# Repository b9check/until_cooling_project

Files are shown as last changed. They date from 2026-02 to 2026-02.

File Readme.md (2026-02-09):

# Organ Perfusion Thermal Control

Simulation of a mobile perfusion system for loading cryoprotective agents (CPA) into porcine kidneys during transport. Developed for Until Labs.

## Problem

Maintain 4°C ± 2°C at the kidney inlet while flow varies 10× (3-30 mL/min) due to pressure control. A flow-dependent transport delay (1-11s) between heater and sensor makes pure PI control fail.

## Solution

Feedforward + PI: feedforward computes heater power from flow rate (P = ṁ·Cp·ΔT), PI trims residual error.

## Results

- Temp max error: 0.23°C (spec ±2°C) ✓
- Pressure max error: 0.87 mmHg (spec ±3 mmHg) ✓

## Files

**Simulation (Task 1):**
- main.m - Full 30-min simulation
- run_simulation.m - Physics + control loop
- heater_dynamics.m - NTU-effectiveness thermal model
- Pure_PI.m - PI without transport delay (baseline)
- Pure_PI_Lag.m - PI with delay, no feedforward (fails)
- plot_dynamics.m - Heater response visualization

**CAD:**
- CAD/Cooling Machine/ - Task 1: Mobile perfusion system
- CAD/Cradle/ - Task 2: Organ cradle

## Author

Brian Check - Stanford MS Aero/Astro

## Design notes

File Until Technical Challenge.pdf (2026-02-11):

# Until Take Home Project

# Brian Check Files available on GitHub (https://github.com/b9check/until_cooling_project/tree/main)

# Presentation Overview

## Task 1: Mobile CPA Loading System 1. Problem Overview 2. System Architecture 3. Controller Design and Simulation 4. Hardware Overview

## Task 2: Cradle Design 1. Task Overview 2. Design Overview 3. BOM

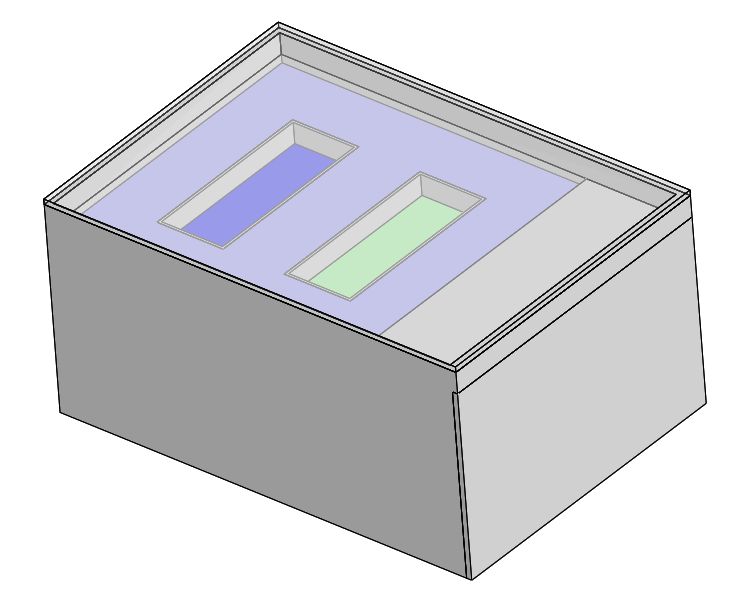
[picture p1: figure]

# Task 1 Mobile CPA Loading System

# Task Overview

## Challenge

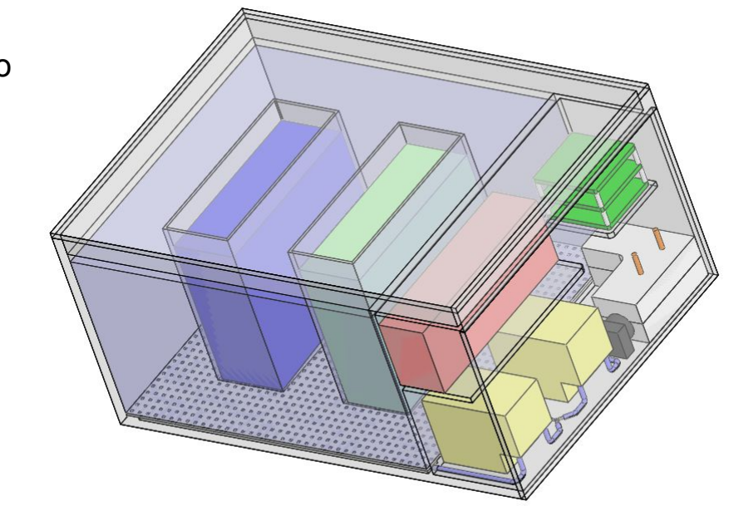
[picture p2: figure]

## - Design mobile system to load cryoprotectants into porcine kidneys during transport

## Requirements - Temperature: 4°C ± 2°C - Pressure: 30 mmHg ± 3 mmHg - Variable flow: 3-30 mL/min - Two-fluid mixing a. Carrier + CPA, ramping up CPA over time - Single-pass perfusion - ~2 hour runtime, battery powered

# Domain Research and Benchmarking

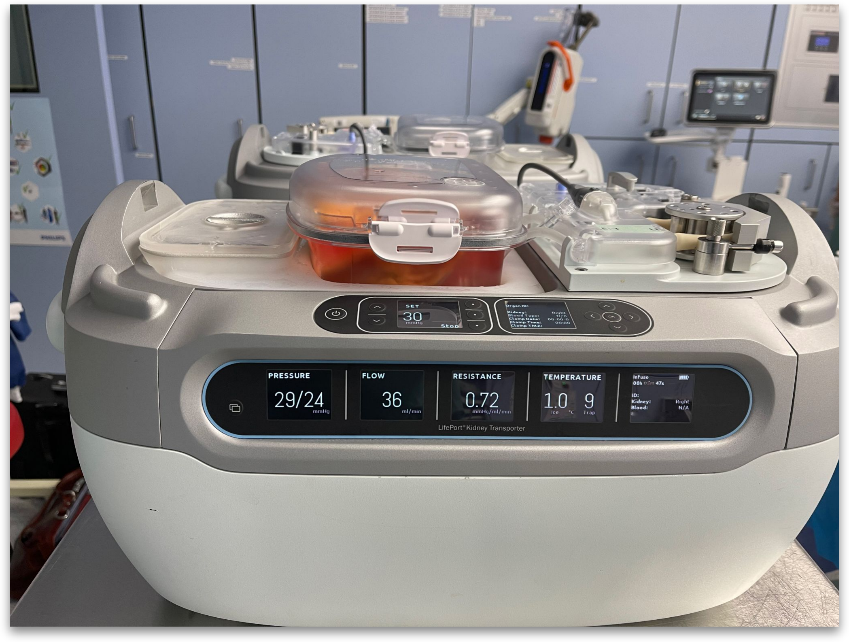
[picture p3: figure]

LifePort Kidney Transporter (https://www.organ-recovery.com/lifeport-kidney-transporter/) - gold standard for clinical kidney transport

## - Pulsatile flow, pressure control, recirculating - Passive cooling with ice bath

## LifePort keeps organs cold, but doesn't meet Until's requirements:

## - Cooling: passively controlled, ~2-10°C (not 4±2°C precision) - Recirculating flow (not single-pass) - Limited to hypothermic preservation (no CPA loading capability)

Key Takeaway: Until's challenge requires active temperature control with single-pass perfusion during CPA concentration ramping
- fundamentally different operating regime than existing clinical transporters

# System Architecture

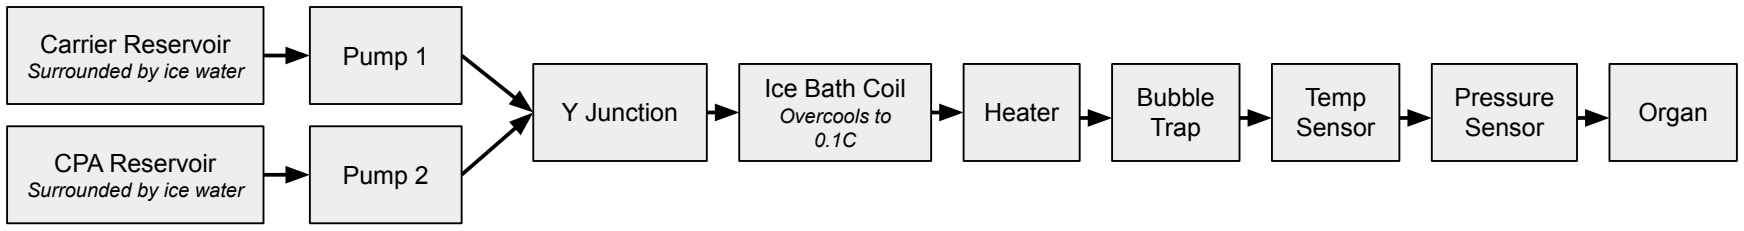
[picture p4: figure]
CPA Reservoir; Surrounded by ice water; Carrier Reservoir; Pump 2; Pump 1; Y Junction; Ice Bath Coil; Overcools to 0.1C; Heater; Bubble; Trap; Temp Sensor; Pressure; Sensor; Organ

### How I got here

The Fundamental Challenge
- To hold ±2°C, you need closed-loop control. Closed-loop control requires an actuator you can modulate
- How do you actively control temperature in a fluid line?
- Peltier/TEC: Bulky, power-hungry, complex heat rejection
- Recirculating chiller: Not mobile - requires benchtop equipment
- Variable ice contact: No practical way to modulate heat transfer dynamically

The realization
- Cooling is hard to modulate. But heating is trivial - a resistive heater with PWM gives you precise, instantaneous control.

The architecture flip
- Instead of trying to cool precisely to 4°C, overcool past the setpoint, then heat back up.

# System Architecture - Layout [Overcooling]

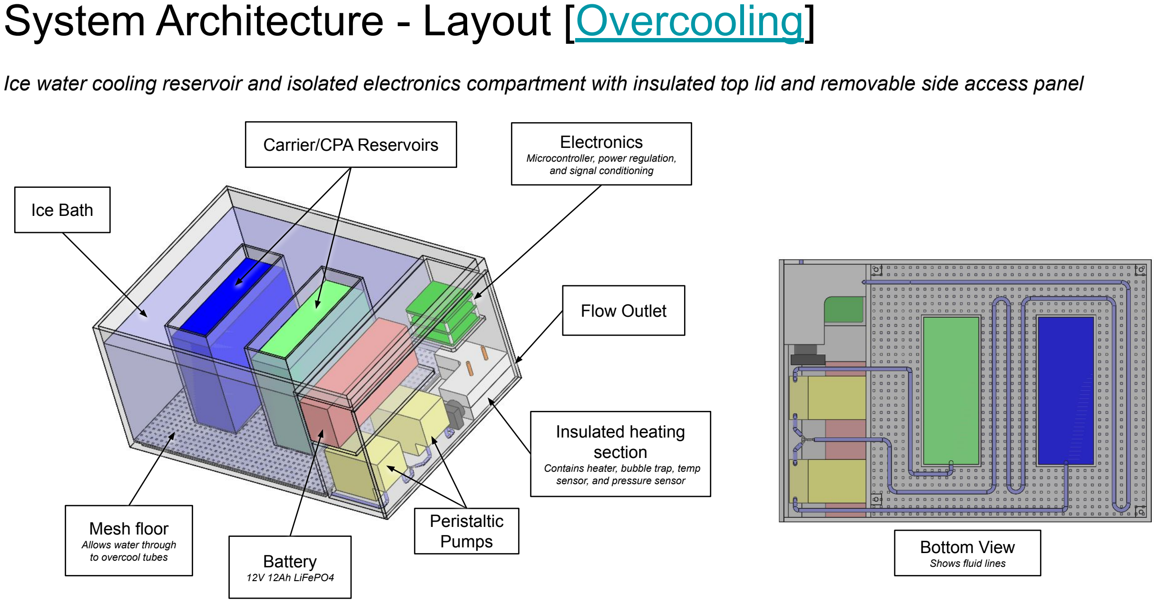
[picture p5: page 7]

Ice Bath

Carrier/CPA Reservoirs

Mesh floor

Allows water through
to overcool tubes

Bottom View

Shows fluid lines

Peristaltic
Pumps

Ice water cooling reservoir and isolated electronics compartment with insulated top lid and removable side access panel

Insulated heating
section

Contains heater, bubble trap, temp sensor, and pressure sensor

Electronics

Microcontroller, power regulation, and signal conditioning

Battery

12V 12Ah LiFePO4

Flow Outlet

# Control: Setup & Challenge

Two independent control loops:

- Pressure → Pump speed (sets flow rate)
- Temperature → Heater power (compensates for varying flow)

Challenge: Flow varies 10x during protocol - heater must maintain 4°C regardless despite temp being coupled with flow speed

# Simulation Setup [Pseudocode]

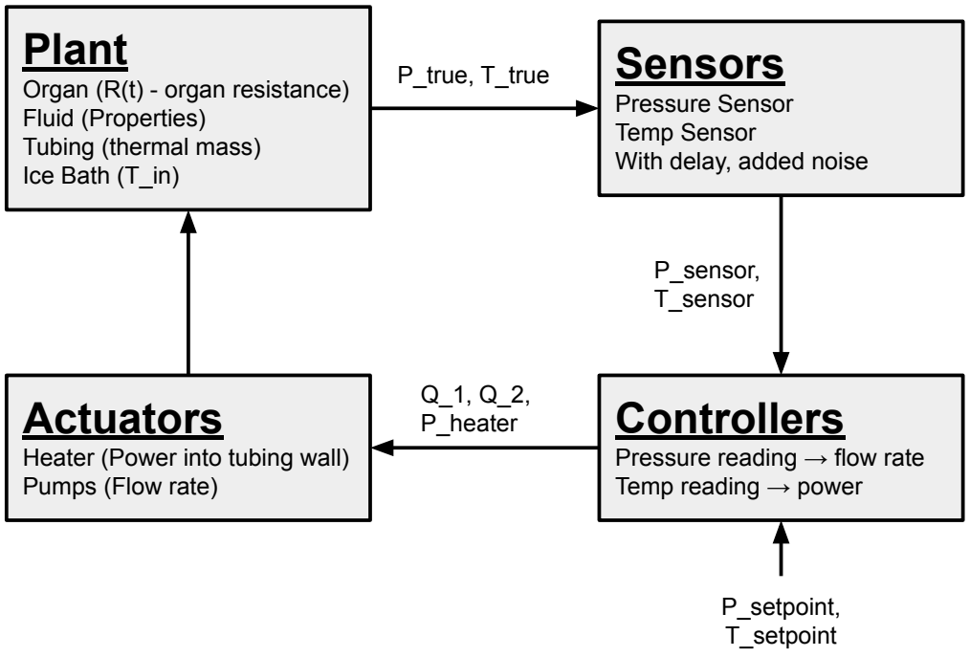
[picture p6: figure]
Plant; Organ (R(t) - organ resistance) Fluid (Properties) Tubing (thermal mass) Ice Bath (T_in); Sensors; Pressure Sensor Temp Sensor With delay, added noise; Controllers; Pressure reading → flow rate Temp reading → power; Actuators; Heater (Power into tubing wall) Pumps (Flow rate); P_true, T_true; P_sensor, T_sensor; Q_1, Q_2, P_heater; P_setpoint, T_setpoint

Setpoints (targets):
- P_setpoint, T_setpoint
Disturbances:
- R(t) - organ resistance changing over time
- T_in - cold fluid from ice bath
Measured (controller inputs):
- P_sensor
- T_sensor
Commanded (controller outputs):
- Q_total → split to pumps
- P_heater → to heater
States (internal dynamics):
- T_wall — tubing wall temperature
- P_integral, T_integral — controller memory Outputs (what you care about):
- P_true — actual organ perfusion pressure
- T_out — actual fluid temperature to organ

# Heat Transfer: Transient Dynamics Model [More Detail]

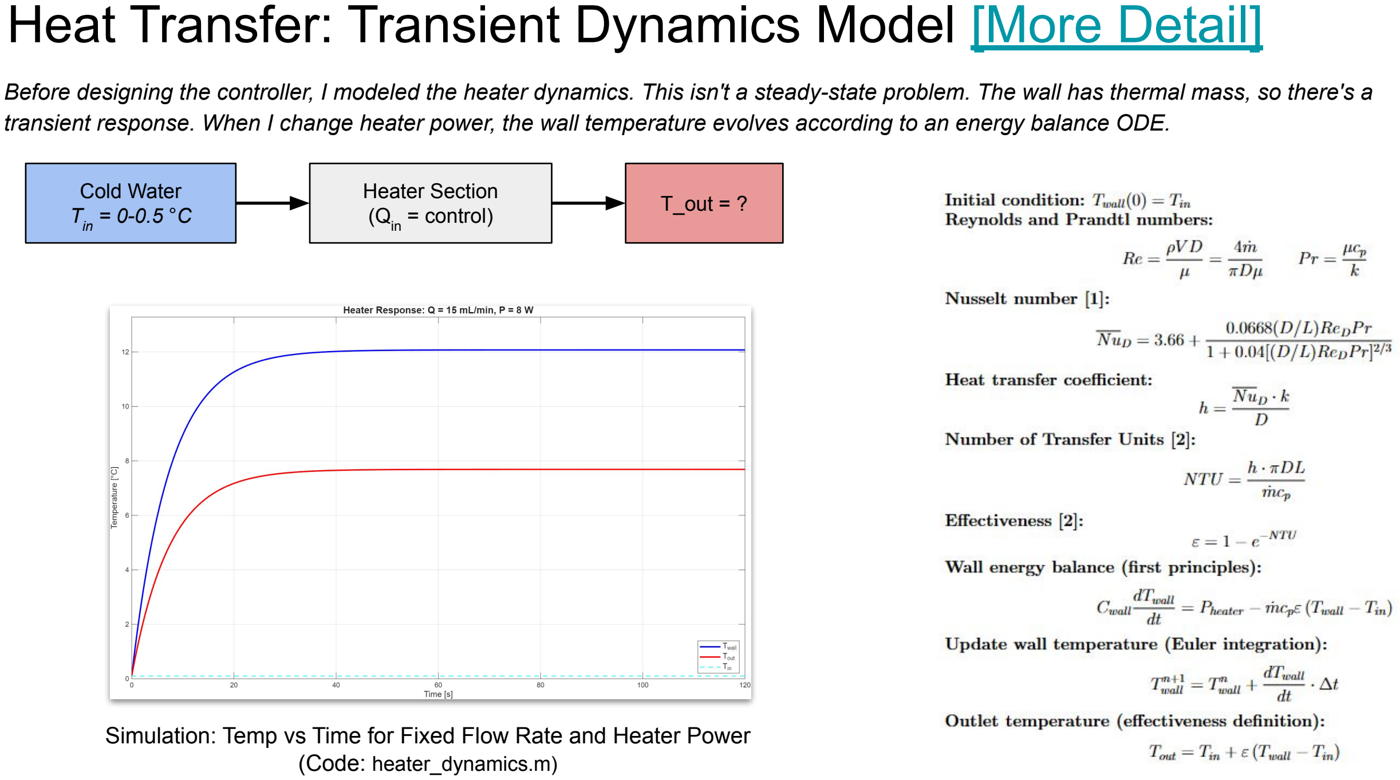
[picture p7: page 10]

Before designing the controller, I modeled the heater dynamics. This isn't a steady-state problem. The wall has thermal mass, so there's a transient response. When I change heater power, the wall temperature evolves according to an energy balance ODE.

Cold Water
Tin = 0-0.5 °C

Heater Section
(Qin = control) | T_out = ?

Simulation: Temp vs Time for Fixed Flow Rate and Heater Power (Code: heater_dynamics.m)

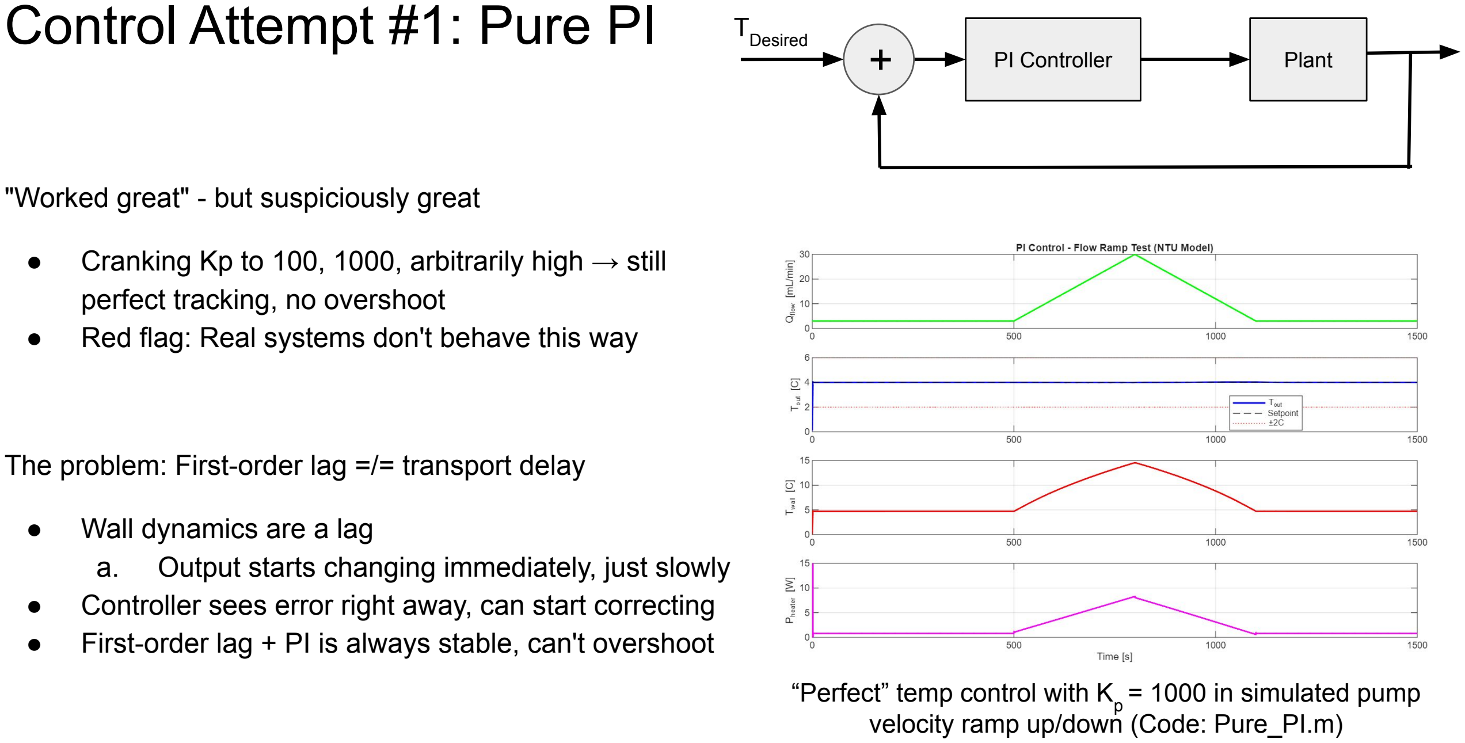
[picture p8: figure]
Control Attempt #1: Pure PI; PI Controller; TDesired; Plant; "Worked great" - but suspiciously great; perfect tracking, no overshoot; ● Wall dynamics are a lag; velocity ramp up/down (Code: Pure_PI.m)

### - Cranking Kp to 100, 1000, arbitrarily high → still

### - Red flag: Real systems don't behave this way

### The problem: First-order lag =/= transport delay

### a. Output starts changing immediately, just slowly - Controller sees error right away, can start correcting - First-order lag + PI is always stable, can't overshoot

### “Perfect” temp control with Kp = 1000 in simulated pump

# Control Attempt #2: Pure PI with Added Transport Delay

A Realization

- Sensor located 8 cm downstream of heater
- Transport delay = tube volume / flow rate
- At 30 mL/min: 1.1 s delay
- At 3 mL/min: 11.3 s delay
- PI now controlling based on stale information
- Variable delay makes tuning impossible - gains that work at high flow oscillate at low flow

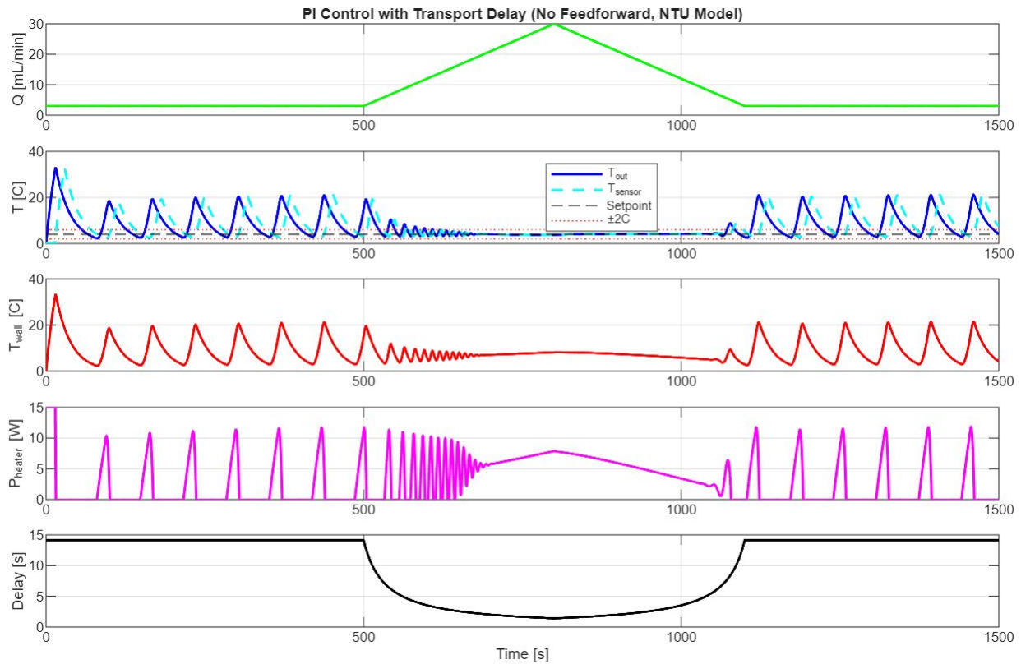
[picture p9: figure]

### Adding delay to sensor input blew up controller (Code: Pure_PI_Lag.m)

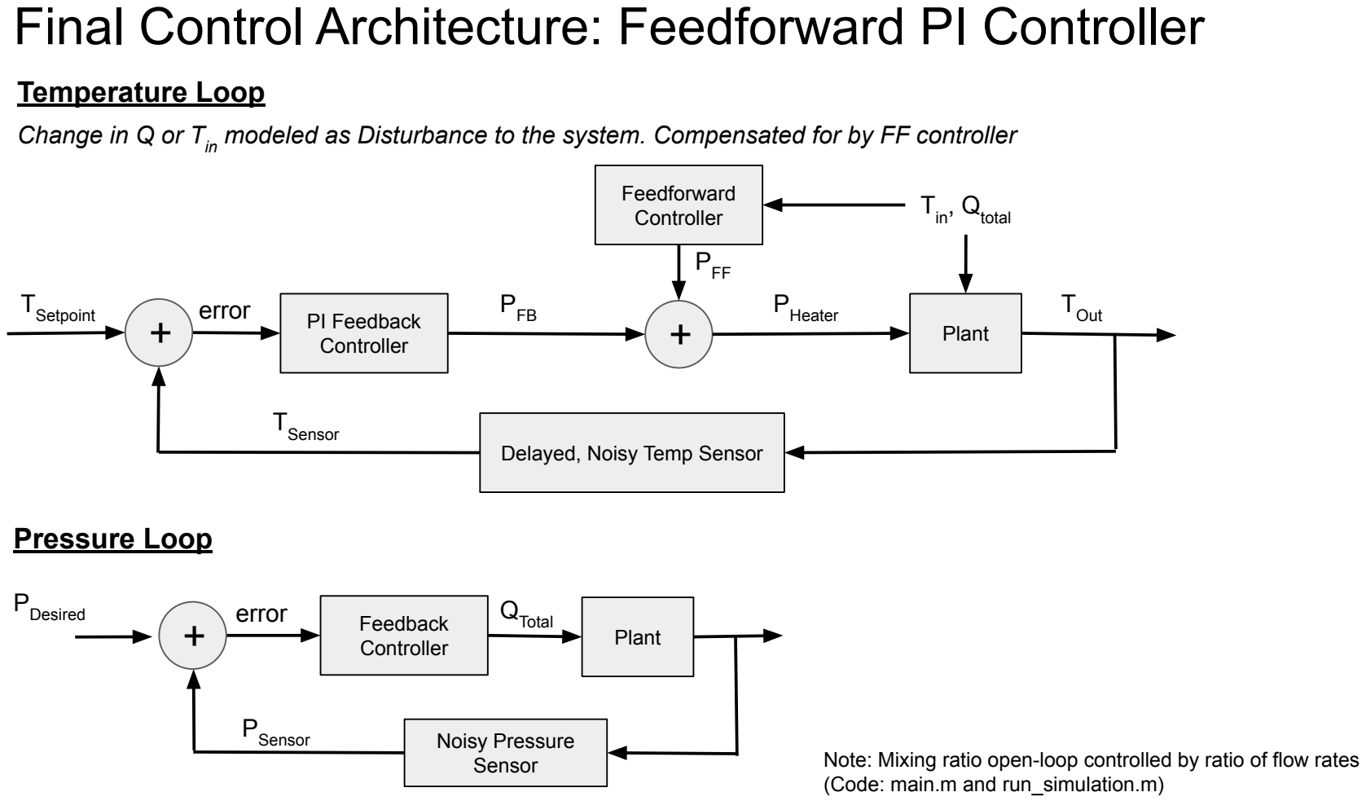
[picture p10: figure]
PI Feedback Controller; TSetpoint; Plant; Tin, Qtotal; Feedforward Controller; Delayed, Noisy Temp Sensor; TOut; Temperature Loop; Pressure Loop; Feedback Controller; PDesired; (Code: main.m and run_simulation.m); Noisy Pressure Sensor; PFB; PFF; PHeater; TSensor; QTotal; PSensor; error

# Final Control Architecture: Feedforward PI Controller

Change in Q or Tin modeled as Disturbance to the system. Compensated for by FF controller

Note: Mixing ratio open-loop controlled by ratio of flow rates

# Simulation Setup

## 30 min protocol: equilibrate → ramp CPA 0→70% Disturbances modeled: - Vascular resistance: 9 → 2 mmHg/(mL/min) (organ relaxes) a. P = Q x R - Pressure adjusts accordingly - Ice bath drift: +1°C over 30 min

- | Sensor noise/bias: Temp (https://pendotech.com/pendotech-products/sensors-and-monitors/temperature-sensors-monitors/) (σ=0.1°C, bias=0.1°C), | pressure (https://www.graylinemedical.com/products/edwards-lifesciences-truwave-disposable-pressure-transducer-kits-tru-wave-single-line-px-disposable-pressure-transduc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) (σ=0.3 mmHg, bias=0.5 mmHg)

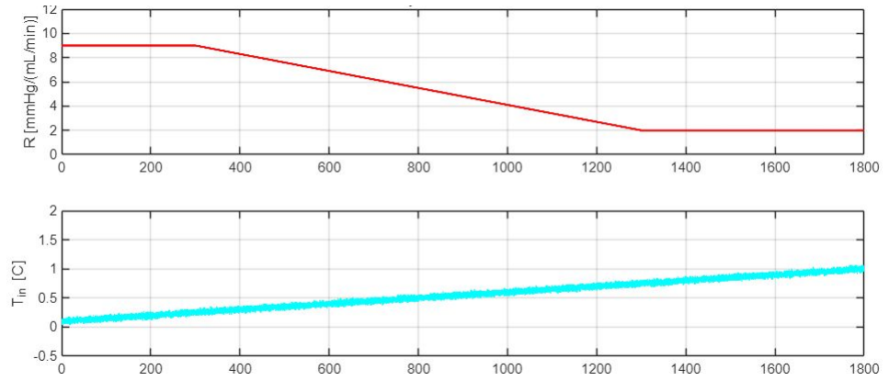
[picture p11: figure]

### Environmental changes to ice bath and organ resistance over simulation

# Simulation Results - Plots

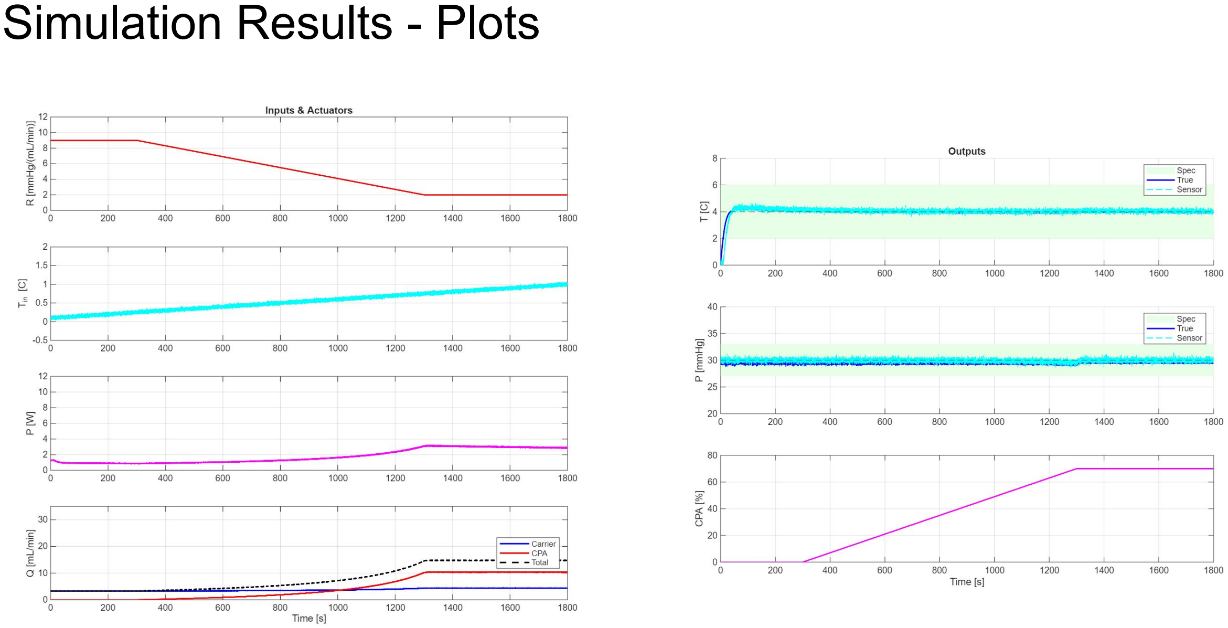
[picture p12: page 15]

# Simulation - Results and Limitations

Metric | Result | Spec
Temp max error | 0.2°C | ±2°C
Temp mean error | 0.06°C | —
Pressure max error | 1.1 mmHg | ±3 mmHg
Pressure mean error | 0.56 mmHg | —
In spec | 100% | —
Heater power | 3.2 W max, 1.8 W mean

### Limitations

- FF uses same thermal model as plant → results are optimistic.

### a. Real system will have model mismatch, would require tuning b. Cp varies with CPA%, heater efficiency - PI gains need tuning on hardware - Not modeled: bubbles, pump pulsation, startup transients - TLDR; have to tune IRL

# Hardware Overview

# Insulated lid, removable electronics panel

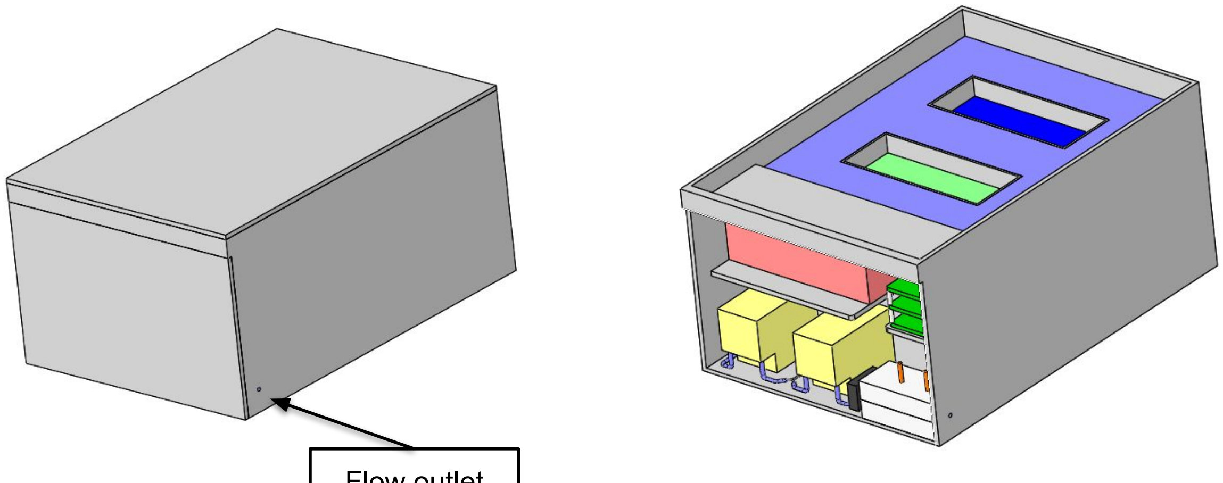
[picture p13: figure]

## Flow outlet

# Hardware Overview - Plumbing (Top view, no ice water)

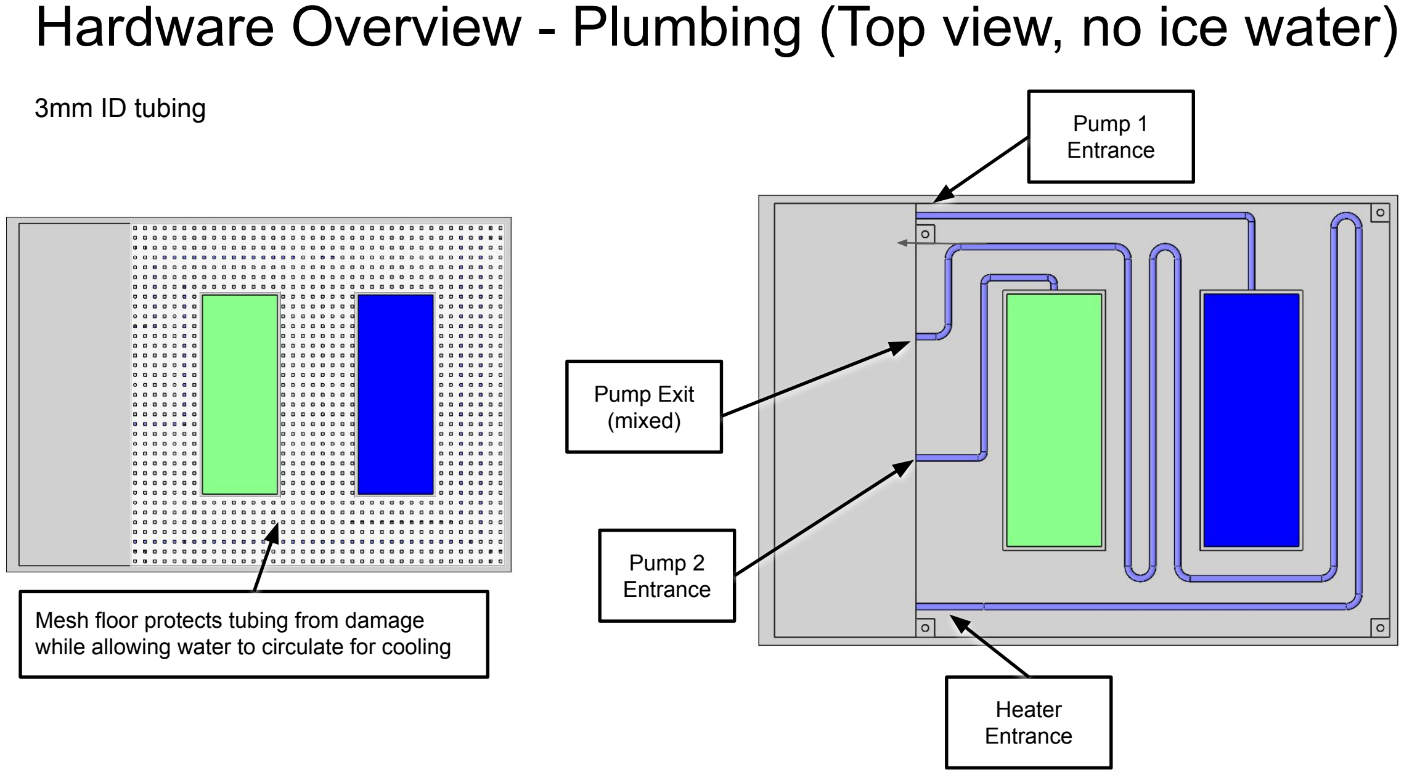
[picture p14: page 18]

Heater
Entrance

Mesh floor protects tubing from damage while allowing water to circulate for cooling

Pump Exit
(mixed)

Pump 1
Entrance

Pump 2
Entrance

### 3mm ID tubing

# Hardware Overview - Electronics

### Components

- Temp Sensor (https://pendotech.com/pendotech-products/sensors-and-monitors/temperature-sensors-monitors/)
- Pressure Sensor (https://www.graylinemedical.com/products/edwards-lifesciences-truwave-disposable-pressure-transducer-kits-tru-wave-single-line-px-disposable-pressure-transduc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)
- Heater (https://keenovo.store/products/keenovo-silicone-heater-strip-pipe-tube-line-heating-band-belt-1) (wrapped around tube)

### - Battery (https://www.dxengineering.com/parts/bip-blf-1212a?seid=dxese1)

- Bubble Trap (https://elveflow.com/microfluidic-products/microfluidics-accessories/bubble-remover/)

### - Y fitting (https://www.mcmaster.com/5372K903/) - T100-WX10 OEM Peristaltic Pump (https://www.longerpump.com/list_62/693.html) - Arduino/ESP32 Microcontroller

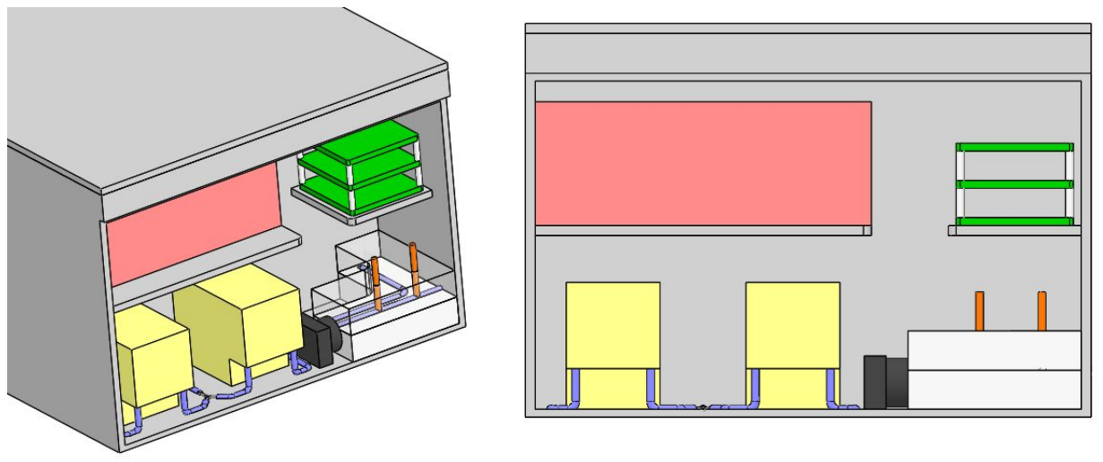
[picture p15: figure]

### Power: 20W typical, 35W max - Heater: 3W - Pumps: 2x 12W max - Controller/Sensors: ~5W

### Size: 14.3" × 20.2" × 9.9"

### Next Steps - Power distribution (12V → 5V/3.3V) - Signal conditioning - Battery charging - Mechanical DFM/DFA

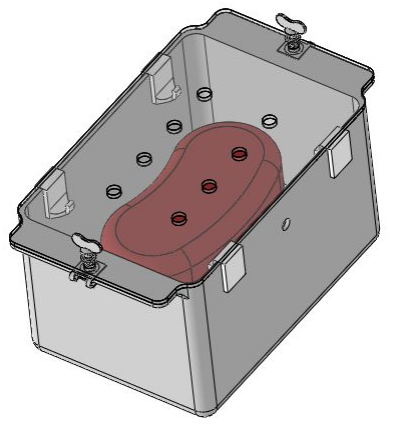
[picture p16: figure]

# Task 2 Cradle

# Task 2

## Requirements

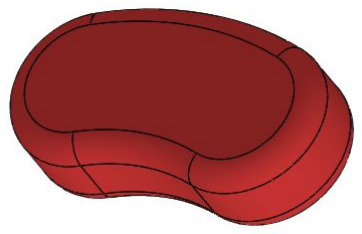
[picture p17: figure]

## - Compliantly hold adult pig kidney in sealed bag - Fit within 8" diameter × 12" length cylinder - 9 sealable ports for fluid/probe access - Arterial cannula at 90° to kidney

## Kidney sizing (3σ range) [Source]

## - Length: 92 - 148 mm - Width: 37 - 77 mm - Thickness: 14 - 41 mm

## Design envelope

## - Fits largest kidney + margin for bag + effluent pool

# Design Overview

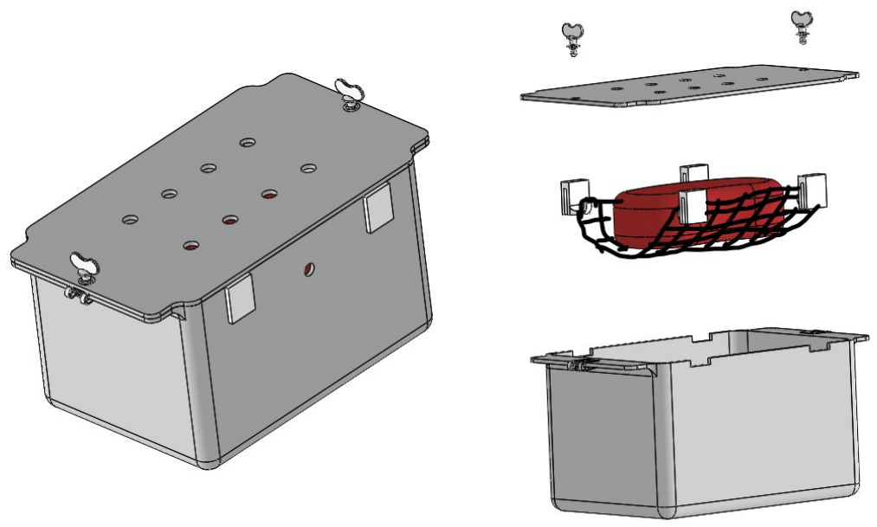
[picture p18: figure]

### Features - Rectangular box with flanged rim - Removable lid with 8 luer ports a. 9th port on side wall - Mesh sling suspended from hooks on rim - Press fit hooks slide onto box - Cannula holder on side wall (90° to kidney) - Quarter-turn latches secure lid

# It Fits! Dimensions: 5.75” x 10” x 5.5”

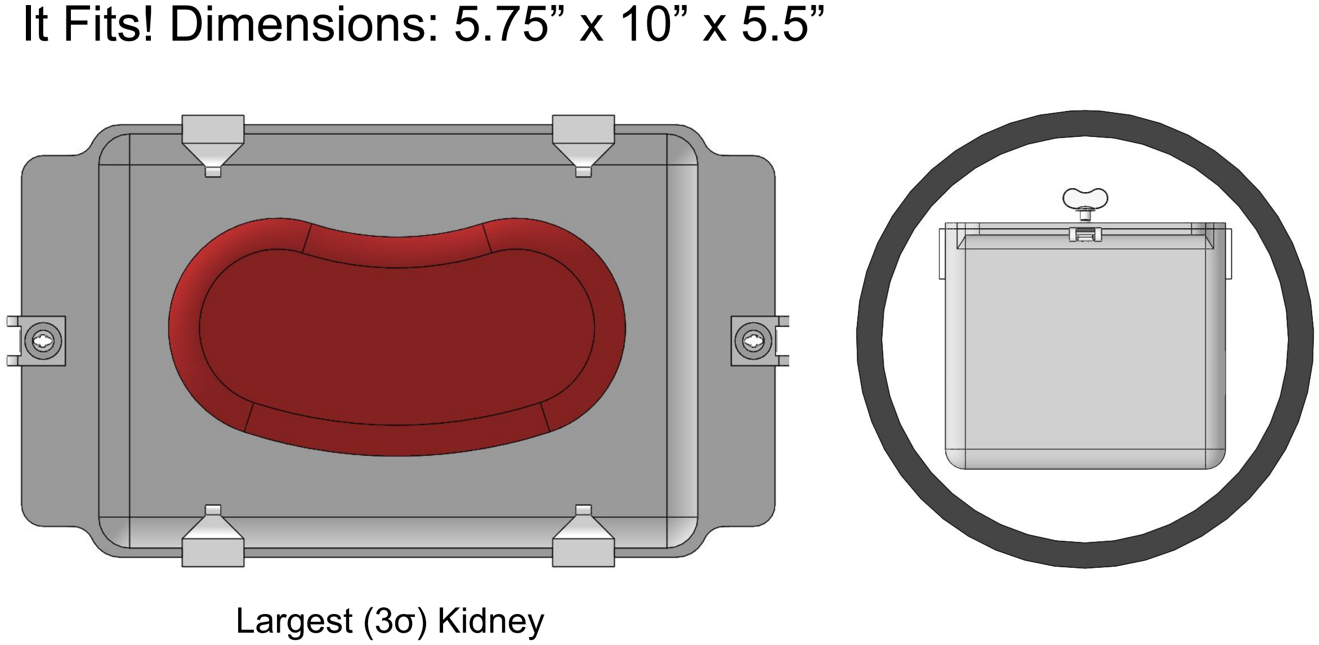
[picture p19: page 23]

# Largest (3σ) Kidney

# BOM, Materials, and Manufacturing

Part | Qty | Prototype Mfg Method | Production Mfg Method
Box | 1 | SLS Tough, print upright | Injection molded PP
Lid | 1 | SLA Tough, print flat | Injection molded PP
Mesh hooks | 4 | SLA Tough, print on side | Injection molded PP
Mesh sling | 1 | Off-the-shelf | Off-the-shelf
Port fittings | 9 | Off-the-shelf luer | Same
Quarter turn fasteners | 2 | McMaster 91382A350 | Off-the-shelf

# Appendix

# Controller Simulation Loop Pseudocode [Go Back]

Inputs
- Set R from protocol schedule
- Set cpa_ratio from protocol schedule → update fluid properties (ρ, Cp, k, μ)
- Update T_in from ice bath model

Pressure control → (True pressure → Pressure sensor reading → Flow speeds)
- P_true = Q_total(i-1) x R
- P_sensor = P_true + bias + noise
- P_error = P_setpoint - P_sensor
- Q_total = Q_nominal + Kp x P_error + Ki x P_integral
- Clamp Q_total to [Q_min, Q_max] with anti-windup
- Split: Q_cpa = Q_total x cpa_ratio, Q_carrier = Q_total x (1 - cpa_ratio)

Temperature control → (True temp → Temp sensor reading → Heater power)
- T_out = heater_dynamics(T_in, T_wall, Q_total, P_heater, fluid, ...)
- delay_samples = V_sensor / Q / dt (quasi-steady approximation)
- T_sensor = T_out(delayed) + bias + noise
- T_error = T_setpoint - T_sensor
- P_ff = ṁ x Cp x (T_setpoint - T_in) (steady-state feedforward)
- P_fb = Kp x T_error + Ki x T_integral
- P_heater = P_ff + P_fb
- Clamp P_heater to [0, P_max] with anti-windup

Plant update:
- T_wall += dT_wall/dt × dt (from heater_dynamics)

# Overcooling [Go Back]

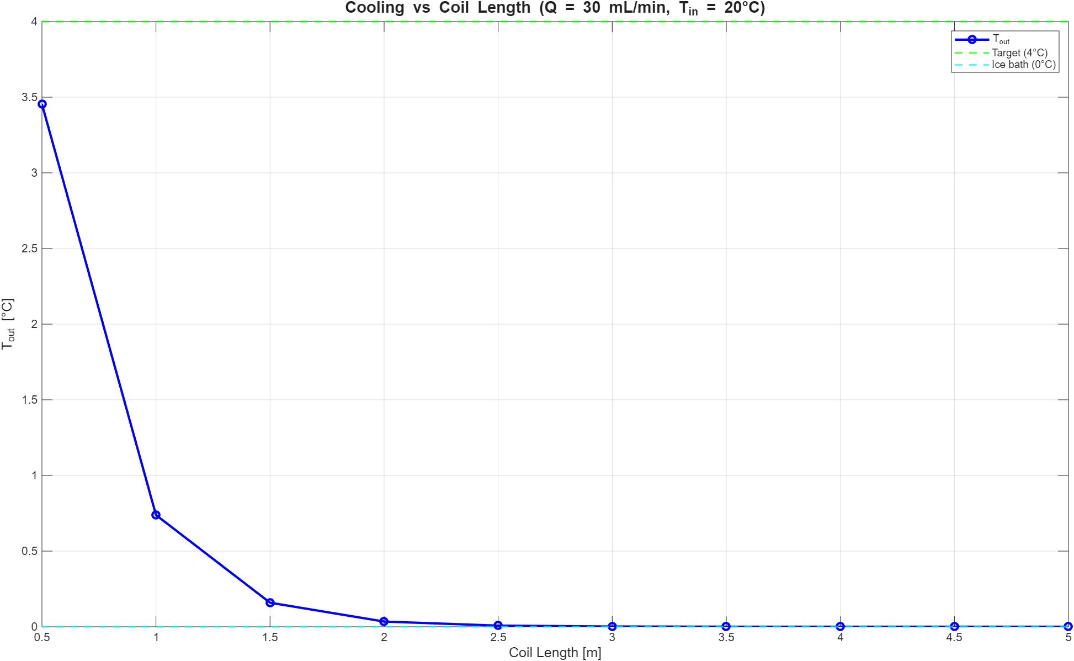
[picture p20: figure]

# 3D Printing Method Selection

| SLS (PA12) | SLA (Resin) | FDM (PLA/ABS)
Strength | High | Low | Med
Surface Finish | Med | High | Low
Watertight | High | High | Low
Large Parts | High | Low | High
Thin Walls | High | Low | Low
Biocompatibility | Med | Med | Low
Tolerance | Med | High | Low
Flexibility | Med | Low | Med

# Heat Transfer Calculations [Go Back]

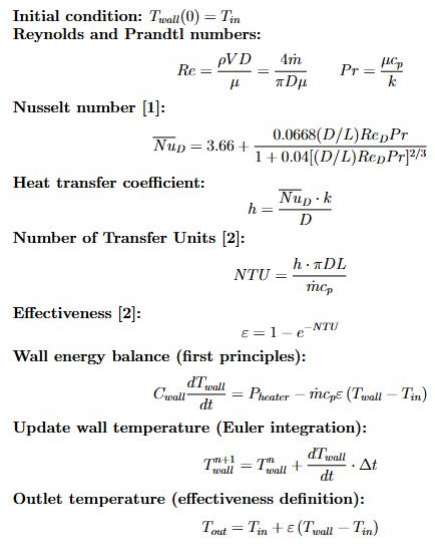
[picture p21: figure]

Inputs:
- Geometry: D (tube diameter), L (heated length)
- Fluid properties: ρ, μ, cp, k (functions of CPA concentration)
- Operating conditions: mdot (mass flow rate), Tin (inlet temperature), Pheater (heater power)
- Thermal mass: Cwall (wall thermal capacitance)

Assumptions:
- Laminar flow
- Fully developed velocity profile, developing thermal profile
- Lumped wall thermal mass (uniform Twall over heater length)
- Negligible axial conduction in fluid
- Cr = 0 (wall thermal capacity ≫ fluid capacity in heater section)

This is a first-principles thermal model. The heater wall has thermal mass - it stores energy. When I apply power, the wall heats up, and heat transfers to the fluid based on the NTU-effectiveness relationship. The key thing is that the dynamics depend on flow rate: at high flow, the fluid pulls heat away faster, so the wall responds differently than at low flow. This is a nonlinear, flow-dependent system.

# Pig Kidney: Worst Case Dimensions (+-3σ) [Go Back]

Dimension | Mean | SD | Smallest (−3σ) | Largest (+3σ)
Length | 120 | 9.2 | 92.4 | 147.6
Width (cranial pole) | 56.9 | 6.7 | 36.8 | 77.0
Width (hilum) | 52.6 | 6.1 | 34.3 | 70.9
Width (caudal pole) | 52.4 | 6.7 | 32.3 | 72.5
Thickness | 27.9 | 4.5 | 14.4 | 41.4

All dimensions in mm
Max: Roughly a 148x77x41 bean

# Sources

1. Incropera, F.P., DeWitt, D.P., Bergman, T.L., Lavine, A.S. Fundamentals of Heat and Mass Transfer, 7th ed., Wiley, 2011, Eq. 8.57, p. 517
a. For heat transfer basics
2. Kays, W.M. \& London, A.L. Compact Heat Exchangers, 3rd ed., McGraw-Hill, 1984, Ch. 2, pp. 19-24
a. For NTU effectiveness calculations to model changing wall temperature
3. Gómez FA, Ballesteros LE, Estupiñán HY. Anatomical study of the renal excretory system in pigs. A review of its characteristics as compared to its human counterpart. Folia Morphologica. 2017;76(2):262–268. doi:10.5603/FM.a2016.0065
a. For pig kidney size

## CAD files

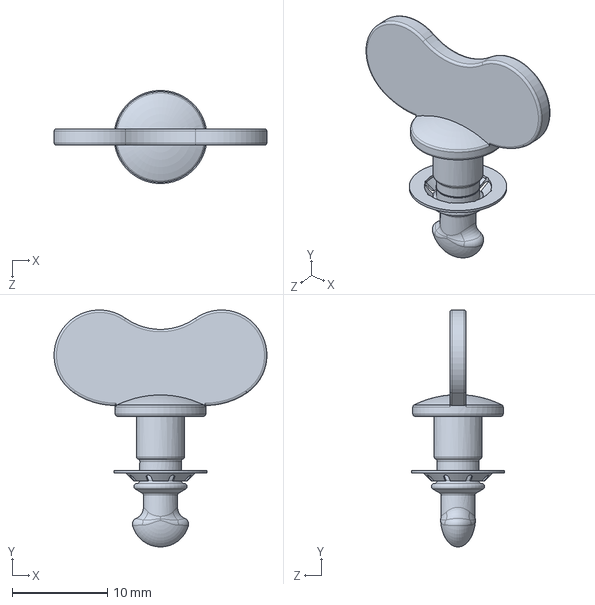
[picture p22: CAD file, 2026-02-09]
CAD/Cradle/Dzus-Fastener.SLDPRT
22.3 x 24.9 x 9.77 mm

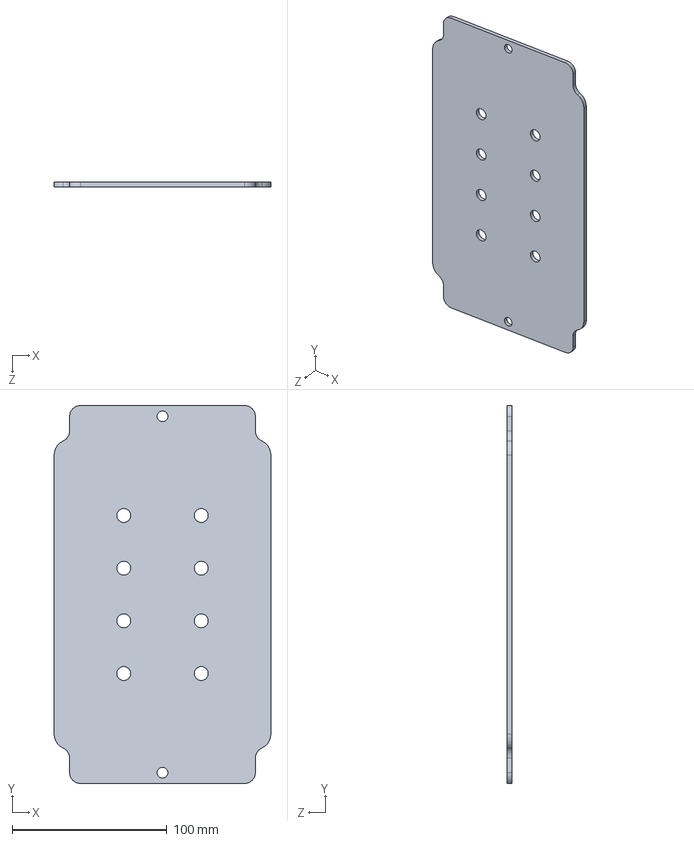
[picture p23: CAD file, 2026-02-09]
CAD/Cradle/cradle_lid.SLDPRT
140.0 x 244.0 x 3.00 mm

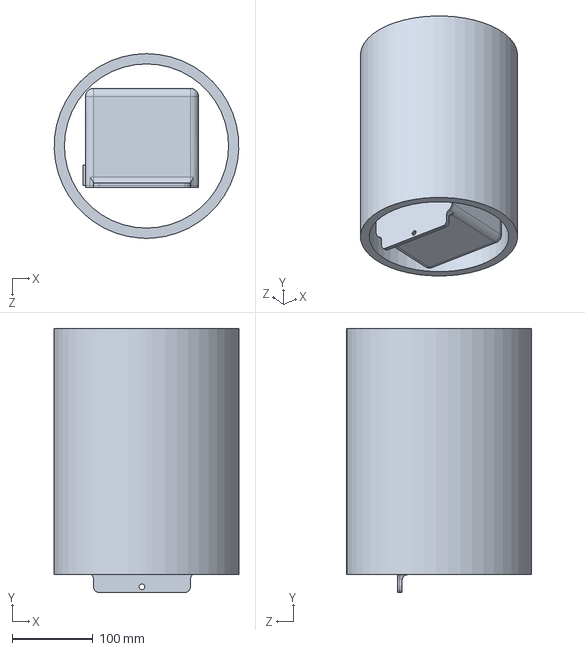
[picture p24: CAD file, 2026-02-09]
CAD/Cradle/cradle.SLDPRT
228.5 x 326.8 x 228.6 mm

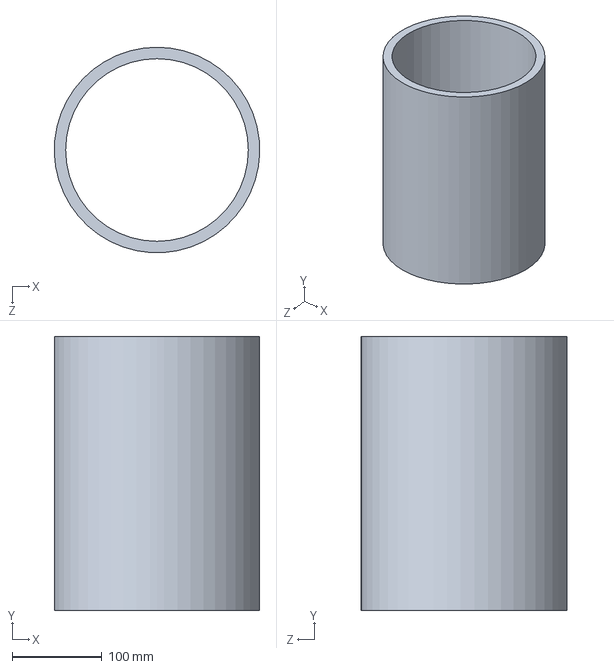
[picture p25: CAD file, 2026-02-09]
CAD/Cradle/cradle_cylilnder.SLDPRT
228.5 x 304.8 x 228.6 mm

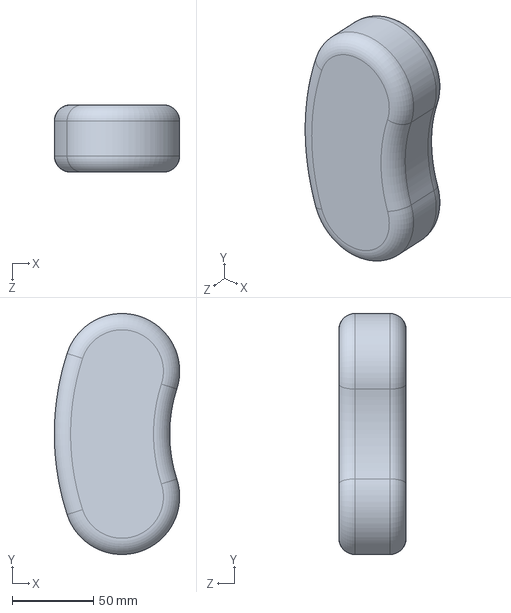
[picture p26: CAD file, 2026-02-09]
CAD/Cradle/kidney.SLDPRT
77.0 x 148.0 x 41.4 mm

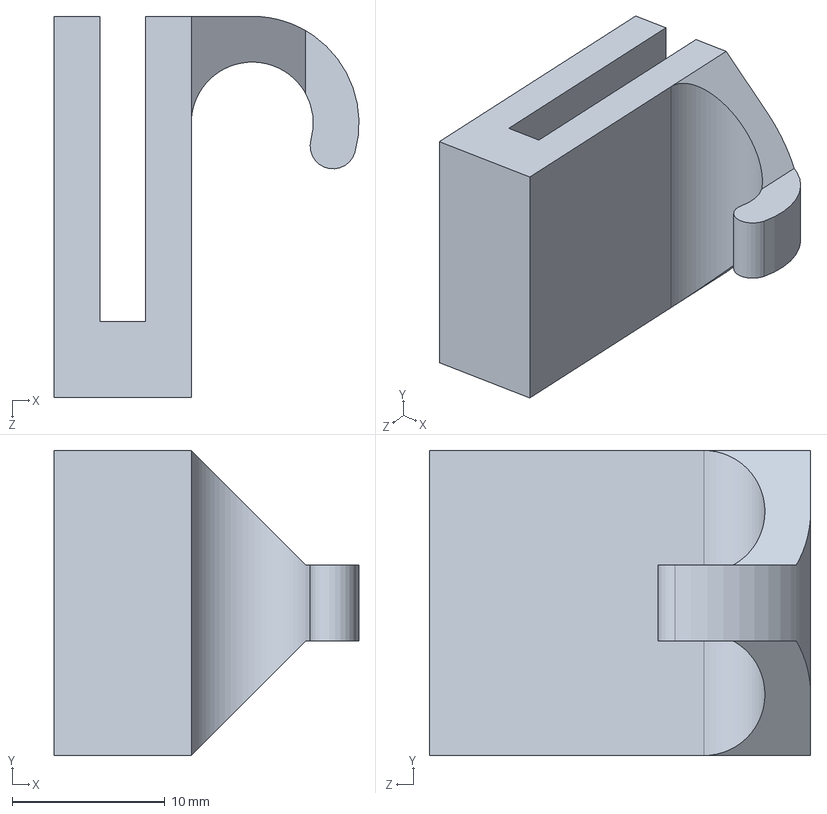
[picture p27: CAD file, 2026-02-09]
CAD/Cradle/hook.SLDPRT
20.0 x 20.0 x 25.0 mm

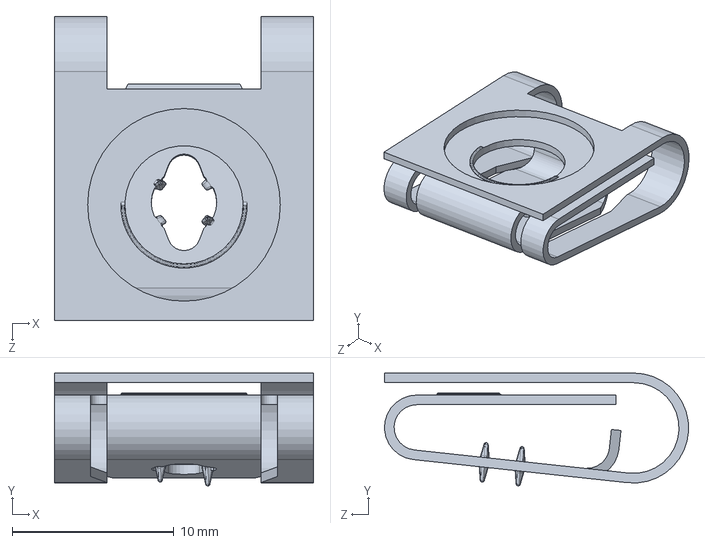
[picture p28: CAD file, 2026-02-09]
CAD/Cradle/Dzus-Clip.SLDPRT
16.0 x 6.98 x 18.8 mm

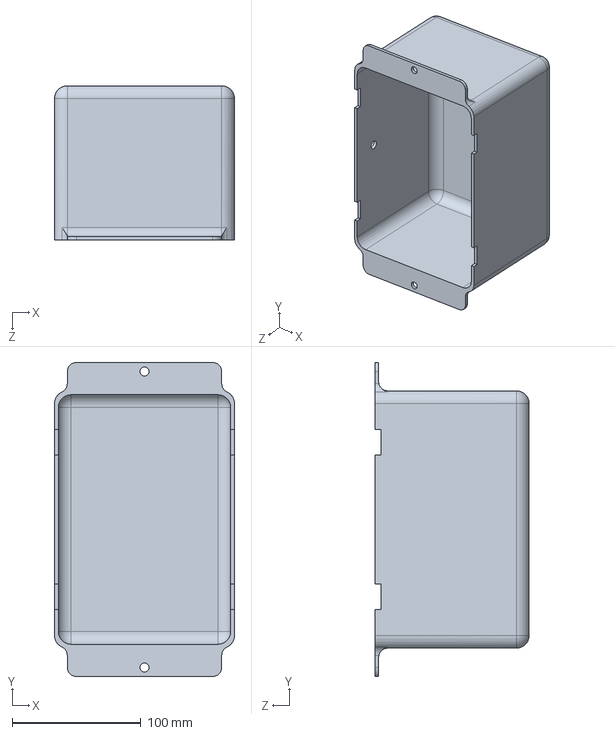
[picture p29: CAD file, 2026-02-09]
CAD/Cradle/cradle_box.SLDPRT
140.0 x 244.0 x 120.0 mm

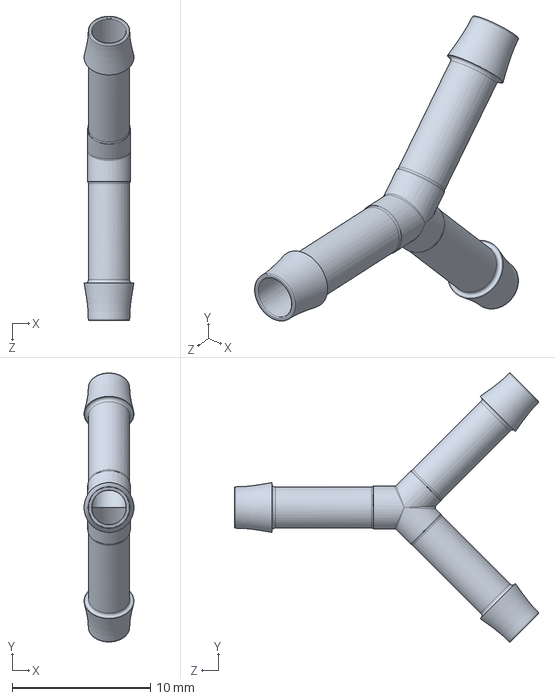
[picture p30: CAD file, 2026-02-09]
CAD/Cooling Machine/5372K903_Plastic Barbed Tube Fitting for Air and Water.SLDPRT
3.61 x 19.5 x 22.0 mm

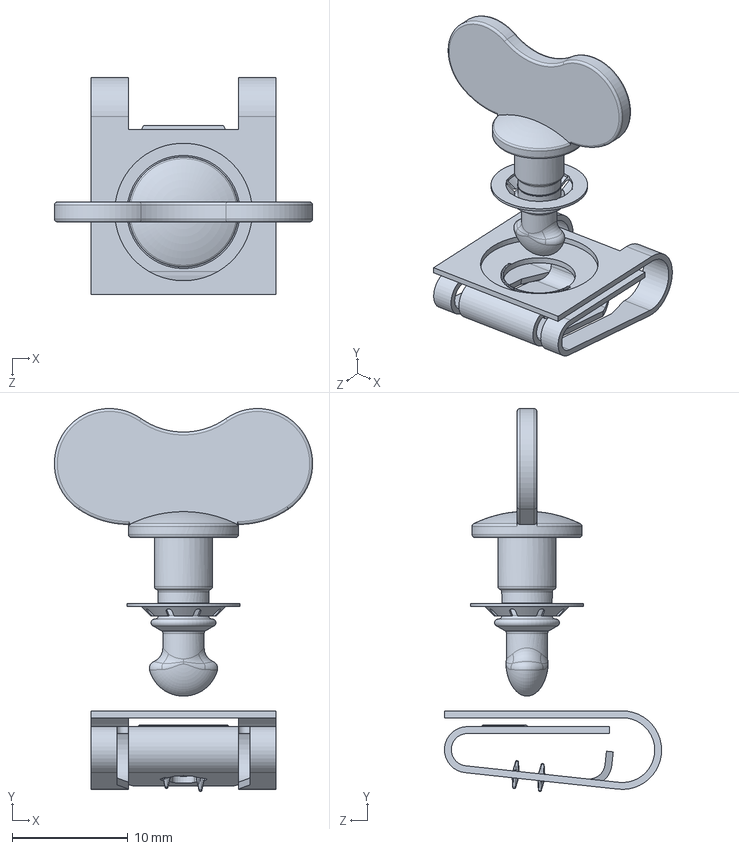
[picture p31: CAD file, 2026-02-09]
CAD/Cradle/91382A350_Zinc-Plated Steel Quarter-Turn Captive Panel Screw.SLDPRT
22.3 x 33.1 x 18.8 mm

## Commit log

2026-02-09 Added CAD, reorganized
    [5372K903_Plastic Barbed Tube Fitting for Air and Water.SLDPRT, 91382A350_Zinc-Plated Steel Quarter-Turn Captive Panel Screw.SLDPRT, Dzus-Clip.SLDPRT, Dzus-Fast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]
2026-02-11 Updated presentation
    [Kidney_Box_assem.SLDASM]
